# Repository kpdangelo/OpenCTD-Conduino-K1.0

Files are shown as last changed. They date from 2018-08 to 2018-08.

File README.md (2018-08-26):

# OpenCTD-Conduino-K1.0
OpenCTD with a Conduino inspired K1.0 graphite conductivity sensor

________________________________________
This CTD sensor started with the Open CTD plan. It evolved with the ideas from the UCSB researchers' Conduino repurposed-micro-USB probe. I was not able to solve the drift and consistency issues with the USB probe, so I have connected an Atlas Scientific K1.0 conductivity probe using the Conduino/AD5933 network analyzer based system. The benefit of using the AD5933 based system is that a calibration is required to convert the probe reading to Conductivity, providing a teaching opportunity on instrumentation. 
________________________________________

This project merges the Oceanography for Everyone Open CTD with the Conduino conductivity sensor, and an Atlas Scientific graphite probe.

Open CTD: https://github.com/OceanographyforEveryone/OpenCTD

Conduino: Marco Carminati, Paolo Luzzatto-Fegiz, Conduino: Affordable and high-resolution multichannel water conductivity sensor using micro USB connectors, In Sensors and Actuators B: Chemical, Volume 251, 2017, Pages 1034-1041, ISSN 0925-4005, https://doi.org/10.1016/j.snb.2017.05.184.

Follow the basic assembly instructions from OpenCTD along with the included instructions for constructing a Conduino.

PCBs can be ordered from OSHPARK, or Eagle and Gerber files are included here. Most of the assembly is with surface mount 0603 components. Doable without a stencil, solder paste and reflow, but easier with.

The system goes into a 2" PVC pipe and seals with Marine Epoxy and a 3D printed plug (file included here). See “Conduino K1.0 Pipe Assembly.pdf” file.

The Conduino PCB contains an analog mux that is not necessary when used with the K1.0 probe. To omit the mux, solder in 0 Ohm resistors R6 and R8 and leave U6 out. The mux was an attempt to zero out the drift seen when using the USB based probe. It didn’t work, but is left in for future experimentation.

The whole thing can be put together for around $300.

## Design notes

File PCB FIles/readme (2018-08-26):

These are the PCB files generated using Autodesk's Eagle CAD package.
*.sch and *.brd - Eagle Files
*.zip - gerbers
pdf's of the schematics too.

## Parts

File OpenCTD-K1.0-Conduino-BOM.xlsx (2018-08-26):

Part | Device | Package | Description
Conduino V03
C1,C4,C8,C16 | 1uF | 0603-CAP | Capacitor | $0.15 | $0.60 | https://www.digikey.com/product-detail/en/tdk-corporation/CGA3E1X7R1C105K080AC/445-12539-1-ND/3954205
C2,C10,C13,C17 | 100nF | 0603-CAP | Capacitor | $0.10 | $0.40 | https://www.digikey.com/product-detail/en/samsung-electro-mechanics/CL10B104KO8WPNC/1276-6582-1-ND/5961441
C9,C12 | 10uF | 0603-CAP | Capacitor | $0.36 | $0.72 | https://www.digikey.com/product-detail/en/samsung-electro-mechanics/CL10A106KP8NNNC/1276-1192-1-ND/3889278
C11 | 47nF | 0603-CAP | Capacitor | $0.22 | $0.22 | https://www.digikey.com/product-detail/en/kemet/C0603C473J4RACTU/399-9095-1-ND/3522612
J4 | BNC | BNC |  | $1.62 | $1.62 | https://www.digikey.com/product-detail/en/te-connectivity-amp-connectors/1-1337543-0/A97553-ND/1755940
R1,R2,R3,R5 | 49.9k | 0603-RES | Resistor | $0.35 | $1.40 | https://www.digikey.com/product-detail/en/panasonic-electronic-components/ERA-3AEB4992V/P49.9KDBCT-ND/3075986
R4,R10 | 20K | 0603-RES | Resistor | $0.19 | $0.38 | https://www.digikey.com/product-detail/en/yageo/RT0603DRD0720KL/311-20KDCT-ND/1035742
R6,R8 | 0 | 0603-RES | Resistor | $0.10 | $0.20 | https://www.digikey.com/product-detail/en/panasonic-electronic-components/ERJ-3GEY0R00V/P0.0GCT-ND/134711
R7 | 180 | 0603-RES | Resistor | $0.35 | $0.35 | https://www.digikey.com/product-detail/en/panasonic-electronic-components/ERA-3AEB181V/P180DBCT-ND/1466034
U1 | AD5933SSOP-16-AD | SSOP-16-AD |  | $35.96 | $35.96 | https://www.digikey.com/product-detail/en/analog-devices-inc/AD5933YRSZ/AD5933YRSZ-ND/756602
U2 | ADA8606-2 | SOIC_N |  | $3.71 | $3.71 | https://www.digikey.com/product-detail/en/analog-devices-inc/AD8606ARZ-REEL7/AD8606ARZ-REEL7CT-ND/3897177
U4 | LP5907 | SOT23-5L |  | $0.65 | $0.65 | https://www.digikey.com/product-detail/en/texas-instruments/LP5907QMFX-3.3Q1/296-40365-1-ND/5178242
U6 | TS3A24157 | VSSOP-10 |  | $1.05 | $1.05 | https://www.digikey.com/product-detail/en/texas-instruments/TS3A24157DGSR/296-22856-1-ND/1740004
PCB |  |  |  | $1.85 | $1.85 | https://www.oshpark.com/shared_projects/RJHBt9SN
OpenCTD-V04
R1 | 4.7K | AXIAL-0.4 | Resistor
U1 | QDUINO_MINI | QDUINO_MINI |  | $29.95 | $29.95 | https://www.sparkfun.com/products/13614
U2 | CONDUINO-V03 | CONDUINO_V03 |  |  |  | See above
U3 | SD-CARD-READER-MICRO-INOUT | SD-CARD-READER-105162 |  | $1.08 | $1.08 | https://www.digikey.com/product-detail/en/molex-llc/1051620001/WM14405CT-ND/6133135
 | Headers for Qduino |  |  | $0.81 | $0.81 | https://www.digikey.com/product-detail/en/sullins-connector-solutions/PPPC121LFBN-RC/S7045-ND/810184
PCB |  |  |  | $8.26 | $8.26 | https://www.oshpark.com/shared_projects/qzoyn3Dc
Pressure Sensor Single PCB
C1 | 0.1uF | 0603-CAP | Capacitor | $0.10 | $0.10 | https://www.digikey.com/product-detail/en/samsung-electro-mechanics/CL10B104KO8WPNC/1276-6582-1-ND/5961441
R1 | 10K | 0603-RES | Resistor | $0.18 | $0.18 | https://www.digikey.com/product-detail/en/panasonic-electronic-components/ERJ-PB3D1002V/P20397CT-ND/6214652
 | Pressure Sensor | MS580314BA01-00 |  | $13.82 | $13.82 | https://www.digikey.com/product-detail/en/sullins-connector-solutions/PPPC121LFBN-RC/S7045-ND/810184
PCB |  |  |  | $0.38 | $0.38 | https://www.oshpark.com/shared_projects/K8ReguM0
Conductivity Sensor
K-1.0 | Atlas Scientific |  |  | $139.00 | $139.00 | https://www.atlas-scientific.com/product_pages/probes/ec_k1-0.html
Temperature Sensor
 | Gikfun DS18B20 |  |  | $8.98 | $8.98 | https://www.amazon.com/gp/product/B00Q9YBIJI/ref=oh_aui_detailpage_o08_s00?ie=UTF8&psc=1
 | 2" Gripper |  |  | $9.39 | $9.39 | https://www.amazon.com/gp/product/B000VYNUAW/ref=oh_aui_detailpage_o08_s00?ie=UTF8&psc=1
 | 2 AH Li-Ion Battery |  |  | $12.50 | $12.50 | https://www.adafruit.com/product/2011
 |  |  |  | Total: | $273.56
Note: PCBs are ordered 3 at a time from OshPark, the single PCB price is shown here
Note: when ordering the batteries from Adafruit, you have to order something else to comply with LiIon shiping rules
 |  |  |  |  | $0.00

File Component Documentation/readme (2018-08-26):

Here are some useful datasheets, readily available, here for convenience

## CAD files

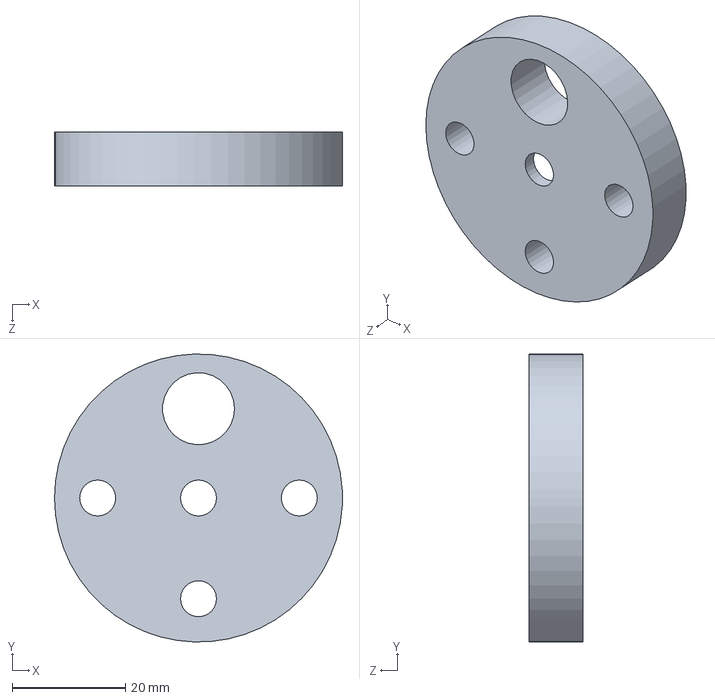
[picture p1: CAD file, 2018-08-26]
3D print/ctd base Pt.SLDPRT
50.8 x 50.8 x 9.53 mm

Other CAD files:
3D print/ctd base Pt.stl

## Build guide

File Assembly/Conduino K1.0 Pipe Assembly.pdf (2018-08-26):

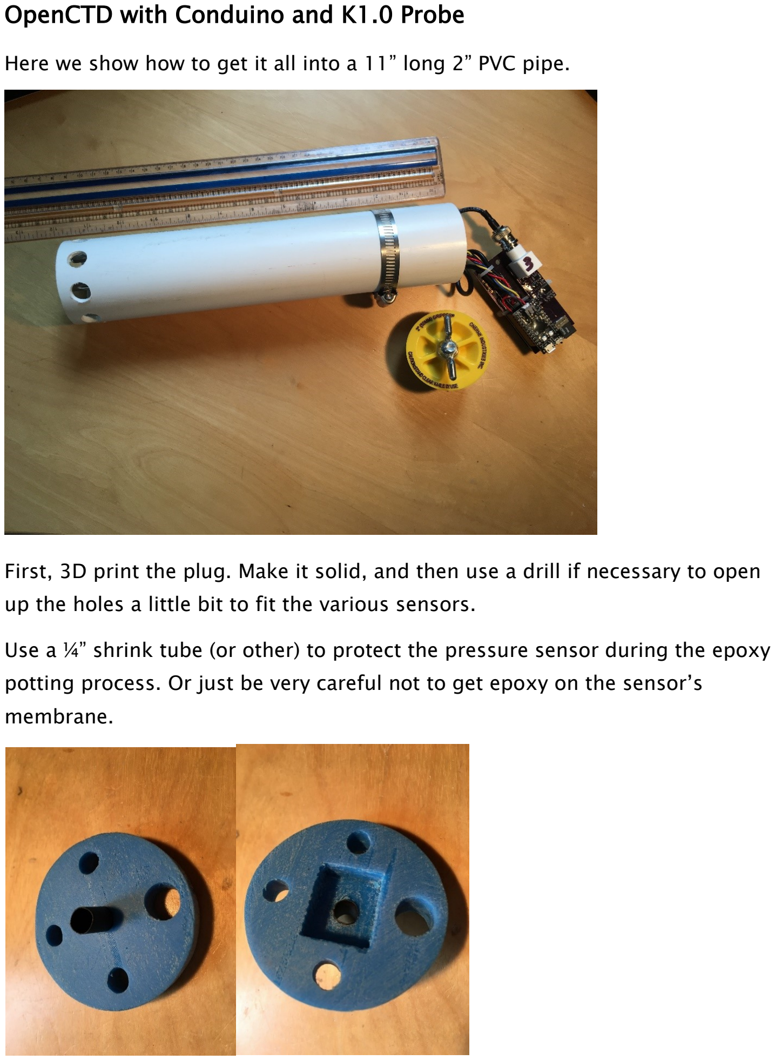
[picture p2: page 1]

OpenCTD with Conduino and K1.0 Probe

Here we show how to get it all into a 11” long 2” PVC pipe.

First, 3D print the plug. Make it solid, and then use a drill if necessary to open up the holes a little bit to fit the various sensors.

Use a ¼” shrink tube (or other) to protect the pressure sensor during the epoxy potting process. Or just be very careful not to get epoxy on the sensor’s membrane.

Secure the pressure sensor PCB in place (use clamps or something), and fill the void which is on the inside of the plug with Marine Epoxy.

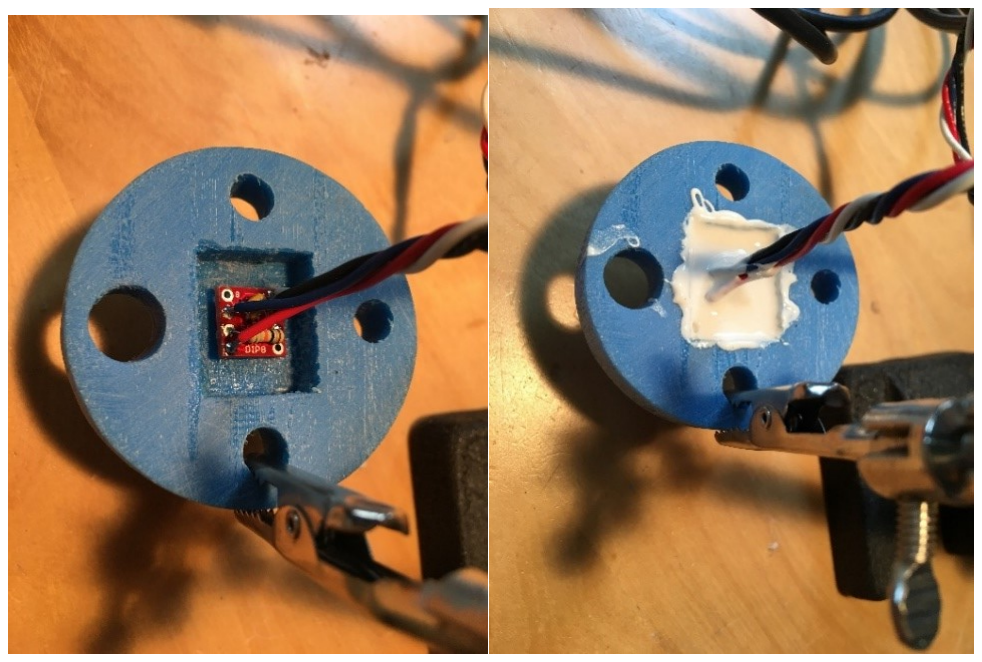
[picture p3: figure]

Next, fit the other sensors and use a little bit of Marine Epoxy to tack them in place, let that dry, and then coat the outside with a generous helping of Epoxy.

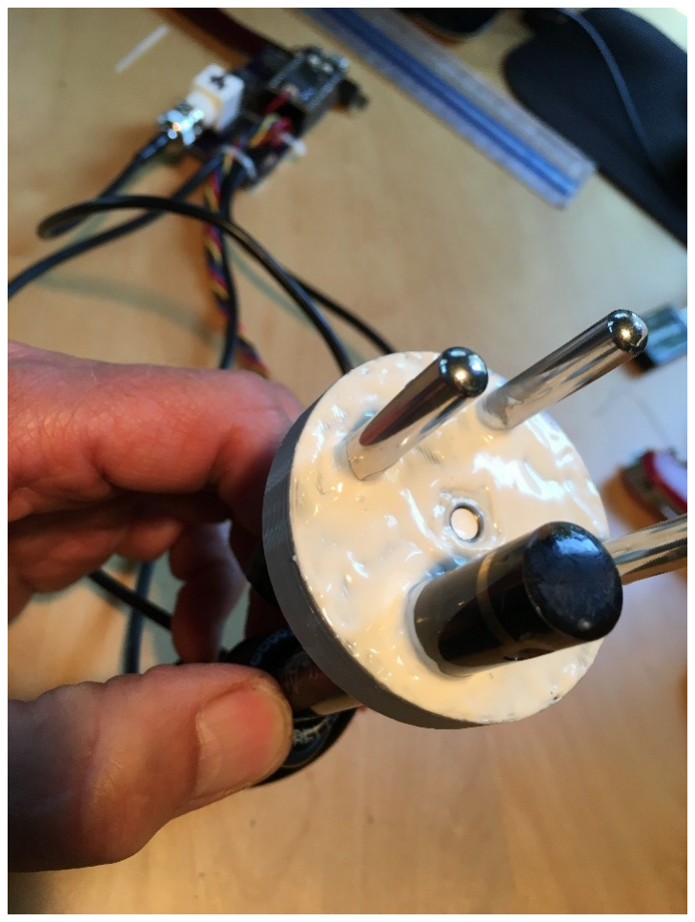
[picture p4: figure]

A nice way to handle the excess coax wire from the conductivity probe is to wrap it around the probe. Do this before you epoxy the base plate into the pipe.

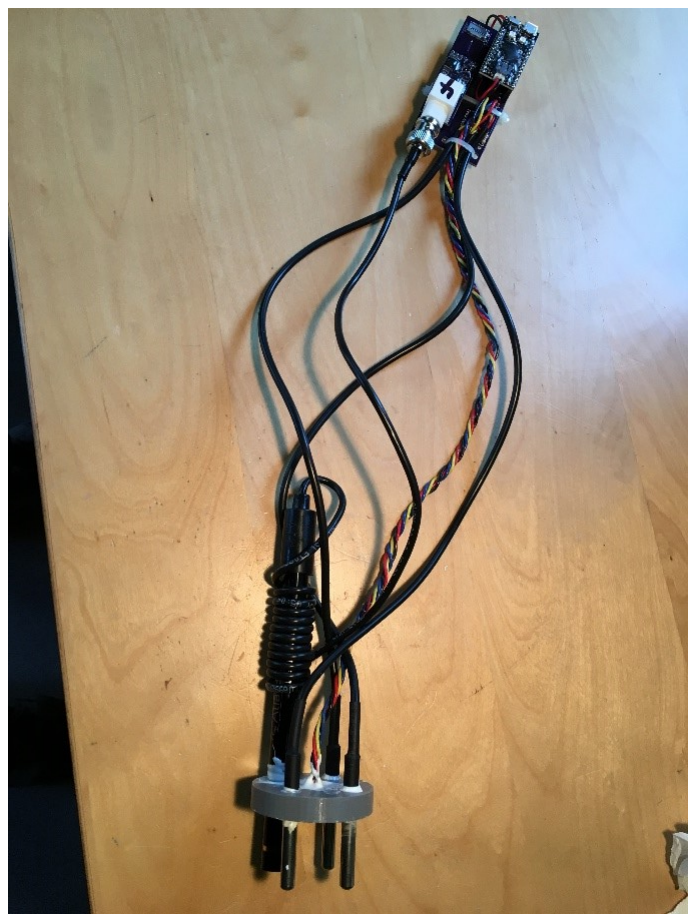
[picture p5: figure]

Epoxy the base plate into the pipe. Then go back and add epoxy so there is a nice seal around the exterior edge.

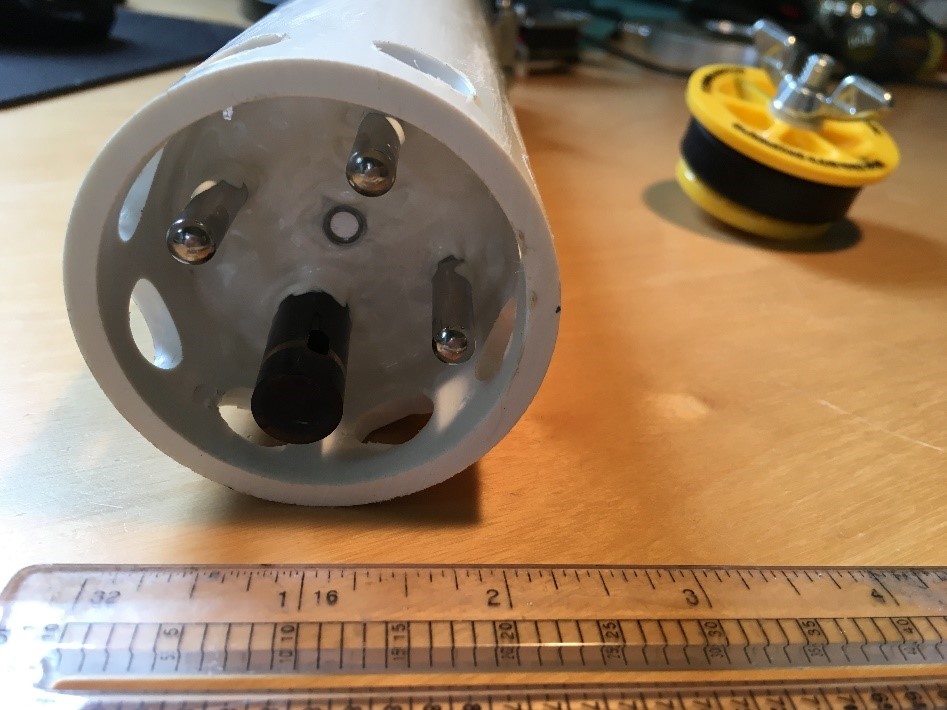
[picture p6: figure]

Cram the circuit board and the wires in the pipe. A twist of the circuit board is helpful to discover a fit. Attach the Gripper Plug and you’re ready to go. A hose clamp is a nice way to attach a cable to the probe.

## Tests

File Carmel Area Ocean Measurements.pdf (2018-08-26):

Carmel Area Ocean Measurements

The CTD sensor was used to sample various points along the Carmel City Beach and around Carmel Point and the Carmel River Lagoon. The region sampled is from 0 to 20 yards out at each location with the sensor hand held and moving about. Turbulence was moderate with breaking waves on the shore at Carmel Beach, but relatively smooth at the State Beach. Santa Lucia and the Dive Spot were heavy with kelp and the Dive spot had considerable surge.

Of note is that 4th street is near Pescadero Creek, which is not flowing to the ocean, but has pooled brackish water. 4th street is also at the beach along the Pebble Beach 10th fairway which is irrigated with reclaimed water. Potential reasons for the slightly lower salinity there.

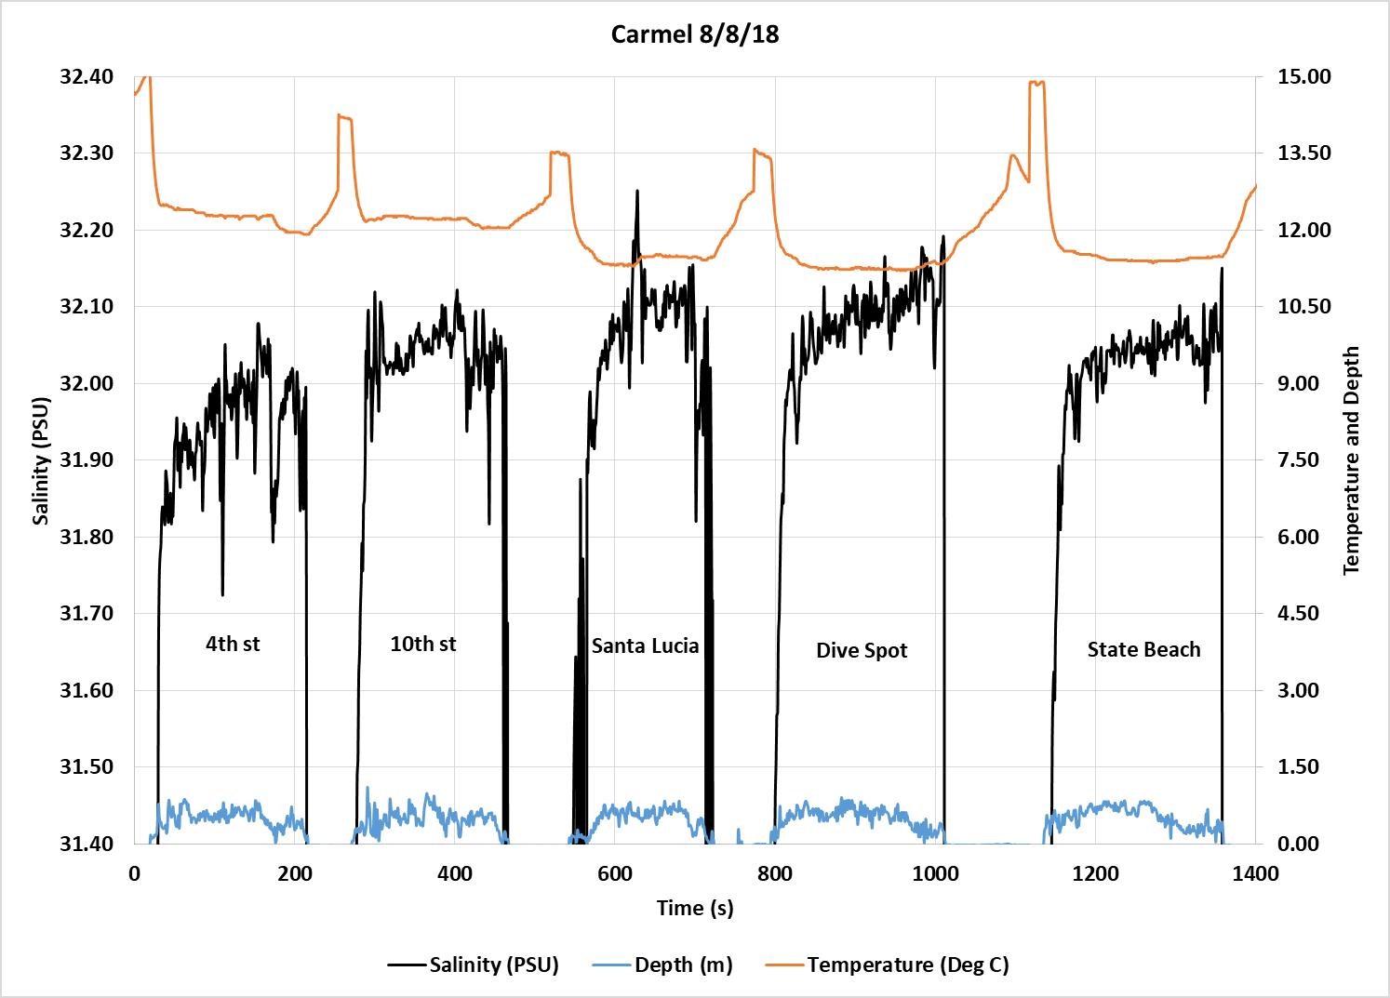
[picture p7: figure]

For fun, the Carmel River Lagoon was also sampled. Water there is not flowing into the ocean, and the surf is not flowing back into the lagoon. The lagoon has been stagnant for 2 months. A steady measurement is shown in the lagoon’s still environment vs. the beach’s breaking waves.

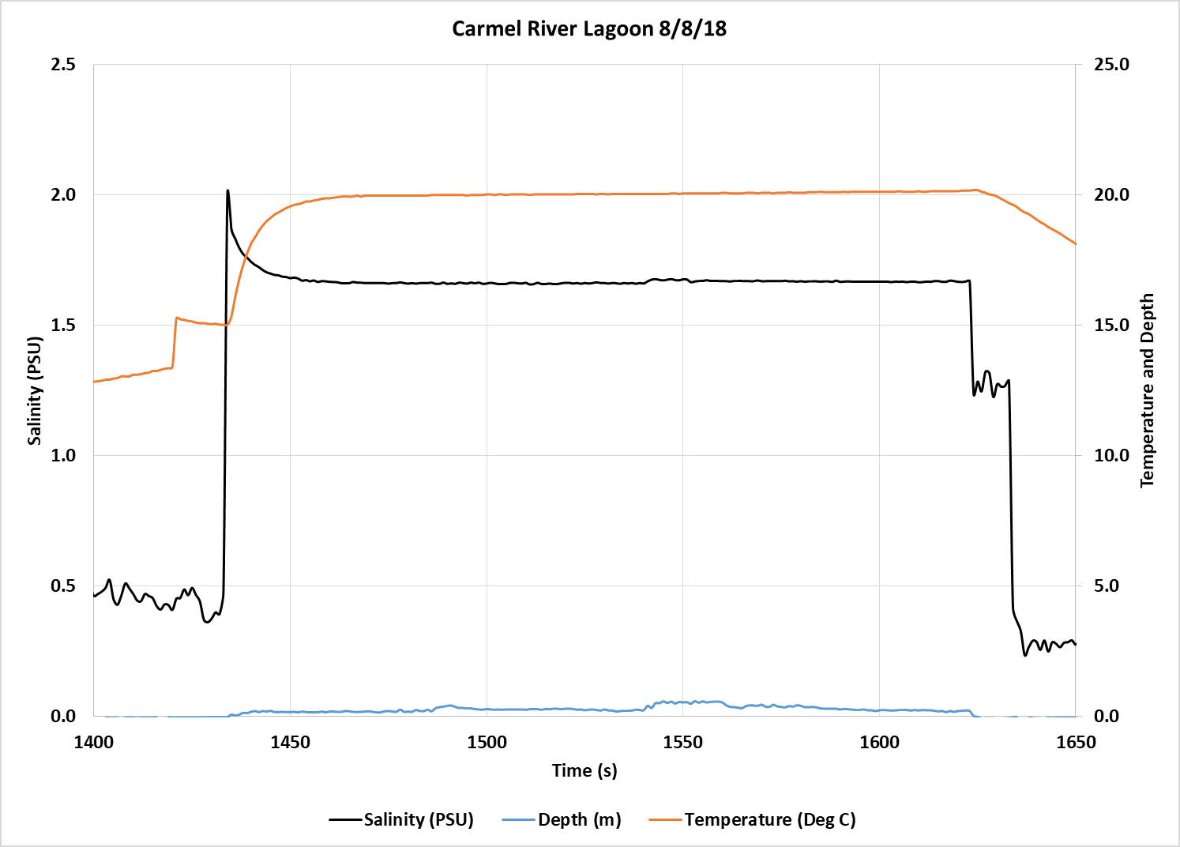
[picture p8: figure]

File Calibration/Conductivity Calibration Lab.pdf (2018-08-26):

Conductivity Calibration Lab

All conductivity sensors require calibration. This is because they use a sensor that measures impedance (a measure of the resistivity of a solution caused by the ions in solution) rather than conductivity directly. In our case we are interested in the conductivity of sea water which we will use to derive a salinity value. Calibration is necessary to develop a curve to translate a raw resistivity measurement into conductivity.

We start with known concentrations of salt in parts per thousand (ppt). The resistivity of the known solution is measured with our probe, and along with temperature and pressure measurements, we can derive the conductivity. We will use 5 different known concentrations to create a curve of conductivity vs. raw resistivity (actually a scaled resistivity to put the numbers in a nicer range). The curve will resemble a straight line, but with a little bit of a bow, so we will use Excel to fit a polynomial curve to it to be more exact in our conductivity vs. raw resistivity transfer function. Then we’ll use that equation to give us conductivity out in the field.

Excel is used to help us keep track of our calibration.

To start, let’s use a table to keep track of the salt concentrations:

First weigh out 110g of Kosher Salt (because it is pure and readily available). Next add water to achieve a given concentration.

For instance, to achieve 40 ppt (0.040 concentration) we need to satisfy the relation in weights (we’ll use grams),

salt
salt + water

= 0.040

A table is super handy so we can use the actual weights used since it’s difficult, and unnecessary to hit the numbers exactly using the scale. Enter the actual weight and let Excel do the concentration calculation.

For this calibration, 110g of salt was used, which resulted in this table:

Concentration | Total Weight | Actual Weight Increment | Target Weight Increment
0.03658 | 3007 | 3007 | 3000
0.03201 | 3436 | 429 | 430
0.02729 | 4031 | 595 | 570
0.02279 | 4826 | 795 | 800
0.01826 | 6025 | 1199 | 1200

Once you’ve added the water and achieved a first known concentration, use a pump inside the vessel, cover it (with foil for example) and let it circulate a good hour or so to let the salt dissolve and the air bubbles to disappear. Use a low power pump so as not to heat the water, or add air.

Turn on the probe, and make sure you get the green light which indicates the micro-SD card is properly seated. Soak the probe at each concentration, adding incremental water for each soak. For the following calibration data, the probe was soaked for 10 minutes at each concentration.

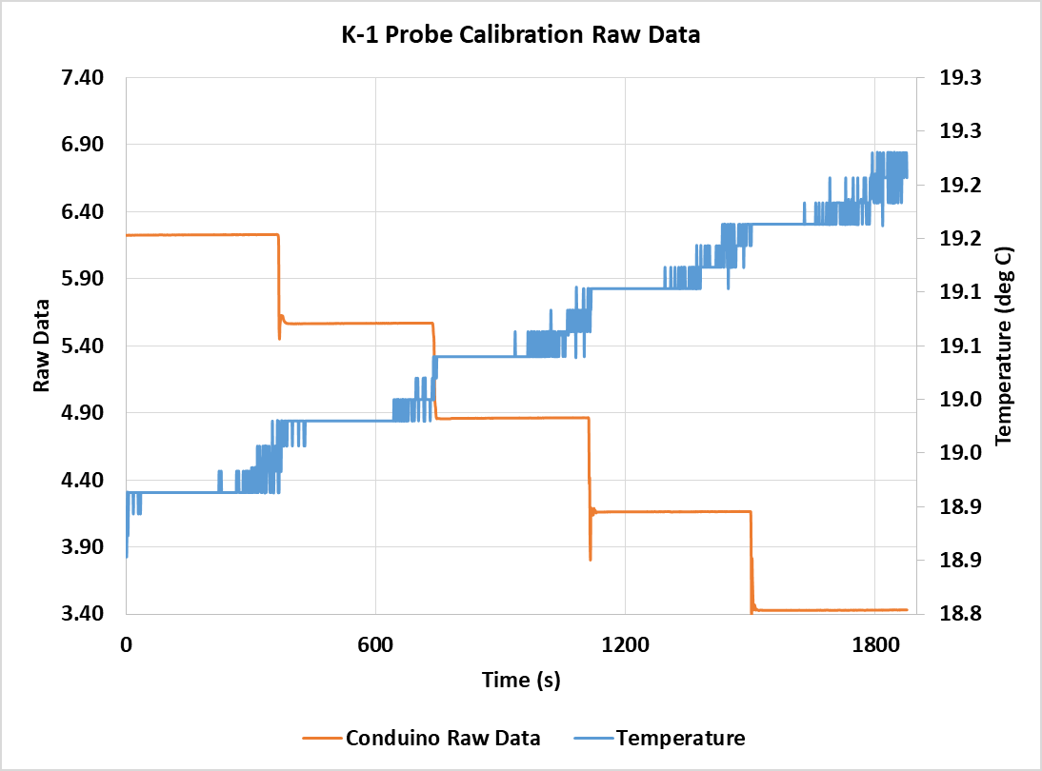
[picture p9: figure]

Here, you can see the orange curve stepping down in resistivity after each increment of water is added. The temperature happens to have a slight upward trajectory which is no big deal.

Next, create a table by translating the known salinity and temperature to conductivity using a calculator at salinometry.com: http://salinometry.com/stp-conductivity-calculator/

For the calculator, enter the known salinity in PPT, enter temperature in degrees C, and pressure in dBar (deci-bar). Our pressure sensor reports in mbar (millibar), so divide that number by 100 (since 1000mBar=10dBar).

Known Salinity (PPT) | temp | Conduino Raw Data | Conductivity (salinometry.com)
18.26 | 19.20 | 3.43 | 26.187
22.79 | 19.13 | 4.16 | 31.981
27.29 | 19.06 | 4.86 | 37.580
32.01 | 18.99 | 5.57 | 43.303
36.58 | 18.93 | 6.229 | 48.717

From this table the transfer function is plotted

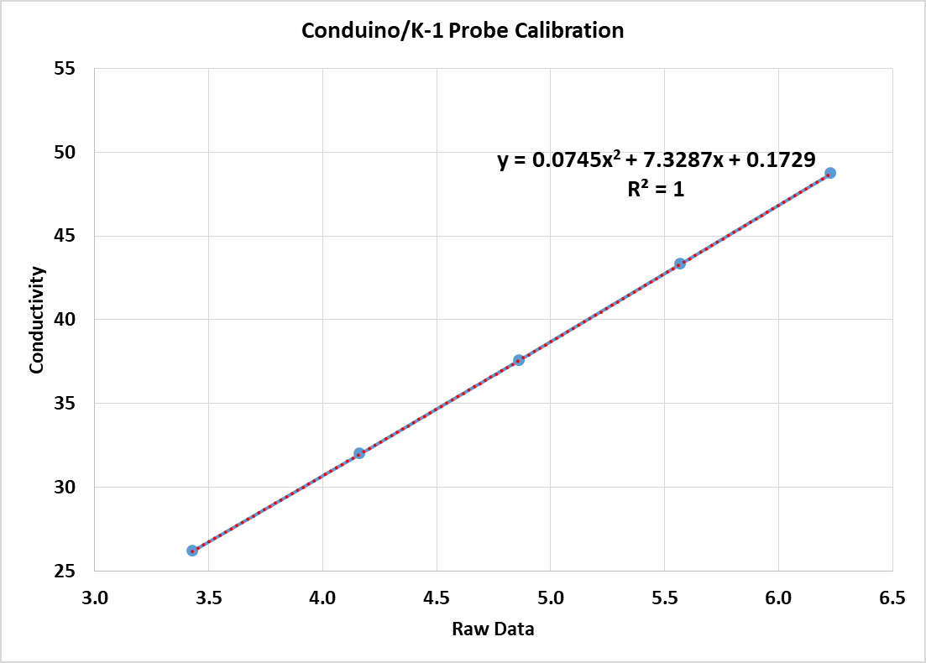
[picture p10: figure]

Here, the “Trendline” feature in Excel is used. You can choose from many options including linear, exponential, power, polynomial, etc. Choose polynomial and you get a great fit. Excel displays R², the coefficient of determination, typically used in statistical analysis where you’re trying to get a curve to represent a cluster of data. When R²=1, it’s as good as it gets.

The equation,

y = 0.0745x

2 + 7.3287x + 0.1729

can now be embedded into the Arduino program resident in the probe electronics to report the conductivity value directly.

After taking the now calibrated probe for a spin in the Carmel surf, and then calculating salinity using the Excel conversion template, we get the following response:

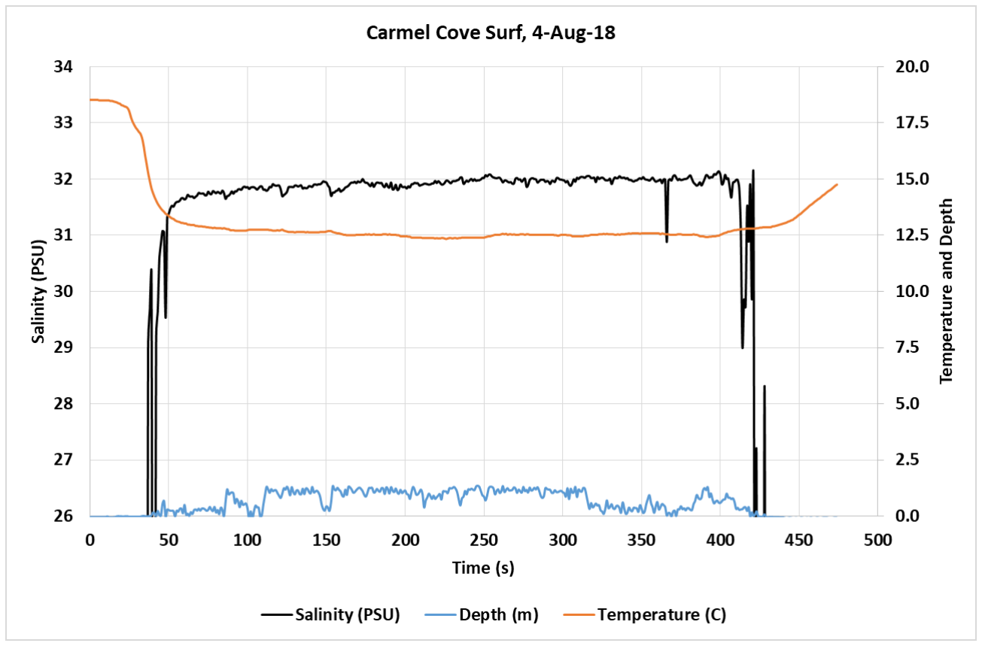
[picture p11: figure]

No surprises here, it’s salty and cold!

8/26/18

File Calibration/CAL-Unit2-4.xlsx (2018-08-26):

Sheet: 2
time | Tave | Conduino | Salt (g) | 110 |  |  | Salinity (PPT) | t1 | Conduino | Conductivity (salinometry.com) | *1,000 | back check: | PSU from Conversion Template | diff | raw data here
0 | 18.9 | 6.26 |  |  |  |  | 18.26 | 19.25 | 3.44 | 26.215 | 26215.2 |  | 19.85 | 8.73% | 0 | 1019.1 | 18.81 | 18.94 | 19 | 48214.42 | 6.2595
1 | 18.9 | 6.26 | Concentration | Total Weight | Actual Weight Increment | Target Weight Increment | 22.79 | 19.18 | 4.18 | 32.016 | 32016.1 |  | 24.83 | 8.96% | 1 | 1019.3 | 18.81 | 18.94 | 19 | 48210.75 | 6.259
2 | 18.9 | 6.26 | 0.03658 | 3007 | 3007 | 3000 | 27.29 | 19.12 | 4.89 | 37.629 | 37628.6 |  | 29.78 | 9.12% | 2 | 1019.1 | 18.81 | 18.94 | 19.06 | 48215.7 | 6.2596
3 | 18.9 | 6.26 | 0.03201 | 3436 | 429 | 430 | 32.01 | 19.05 | 5.60 | 43.359 | 43359.3 |  | 34.83 | 8.80% | 3 | 1019.4 | 18.81 | 18.94 | 19.06 | 48210.75 | 6.259
4 | 18.9 | 6.26 | 0.02729 | 4031 | 595 | 570 | 36.58 | 18.99 | 6.267 | 48.780 | 48780.3 |  | 39.82 | 8.86% | 4 | 1019.3 | 18.81 | 18.94 | 19.06 | 48219.36 | 6.2601
5 | 18.9 | 6.26 | 0.02279 | 4826 | 795 | 800 |  |  |  |  |  |  |  |  | 5 | 1019.1 | 18.81 | 18.94 | 19.06 | 48216.99 | 6.2598
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

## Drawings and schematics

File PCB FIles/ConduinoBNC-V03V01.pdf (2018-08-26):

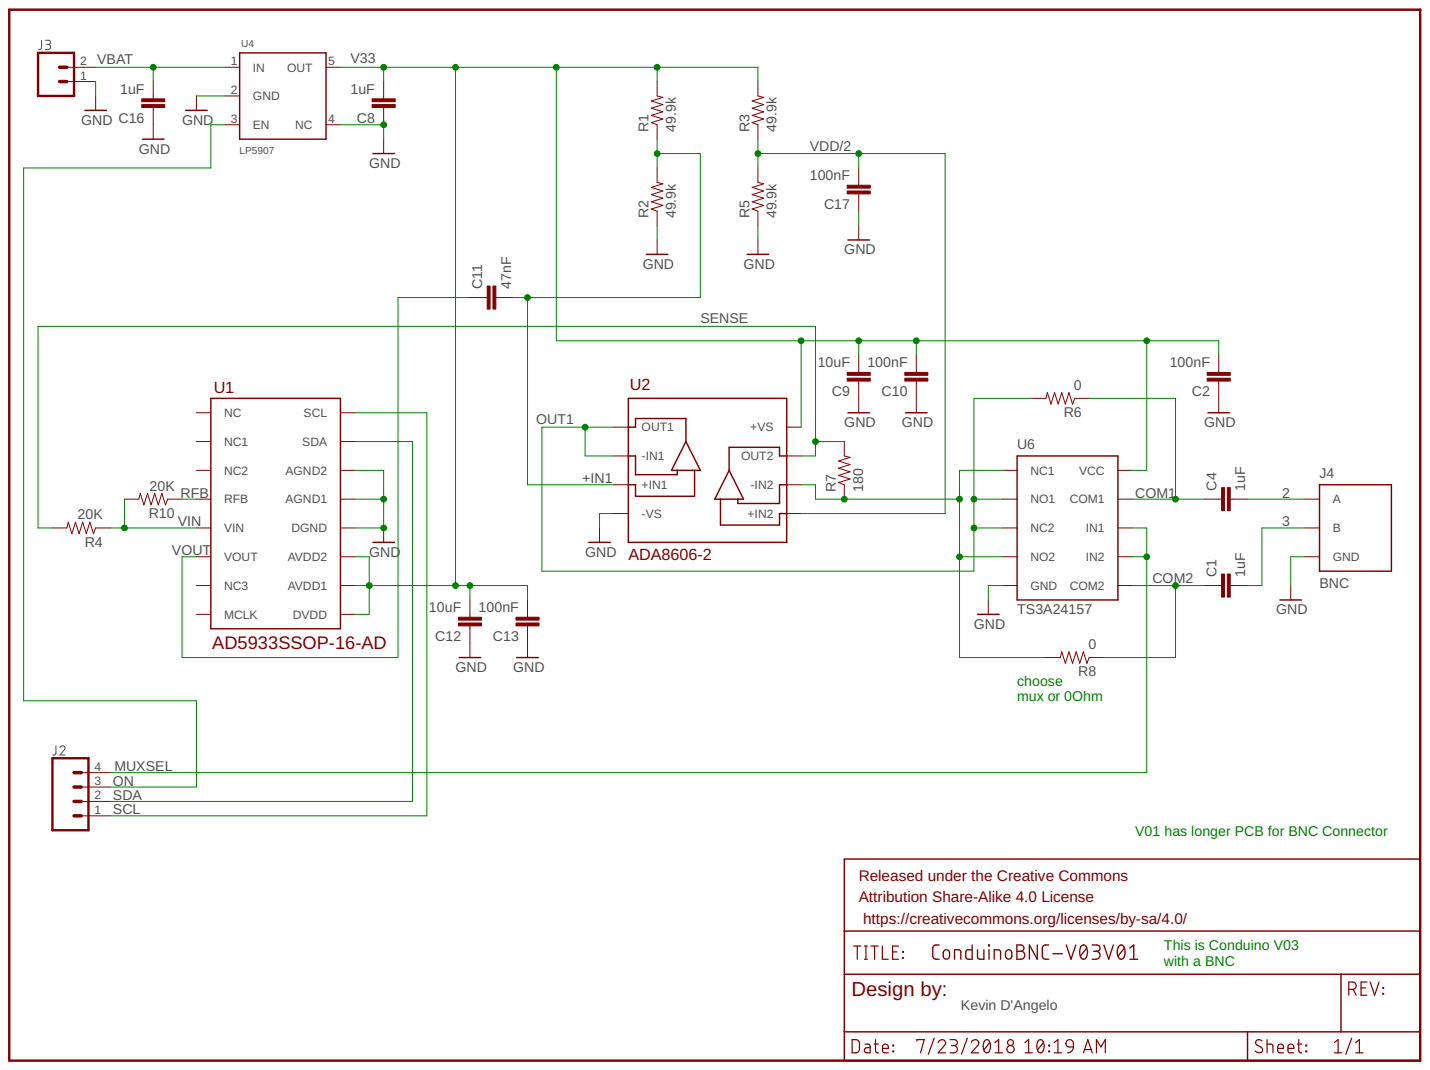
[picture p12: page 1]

V01 has longer PCB for BNC Connector

Released under the Creative Commons Attribution Share-Alike 4.0 License

https://creativecommons.org/licenses/by-sa/4.0/

This is Conduino V03 with a BNC

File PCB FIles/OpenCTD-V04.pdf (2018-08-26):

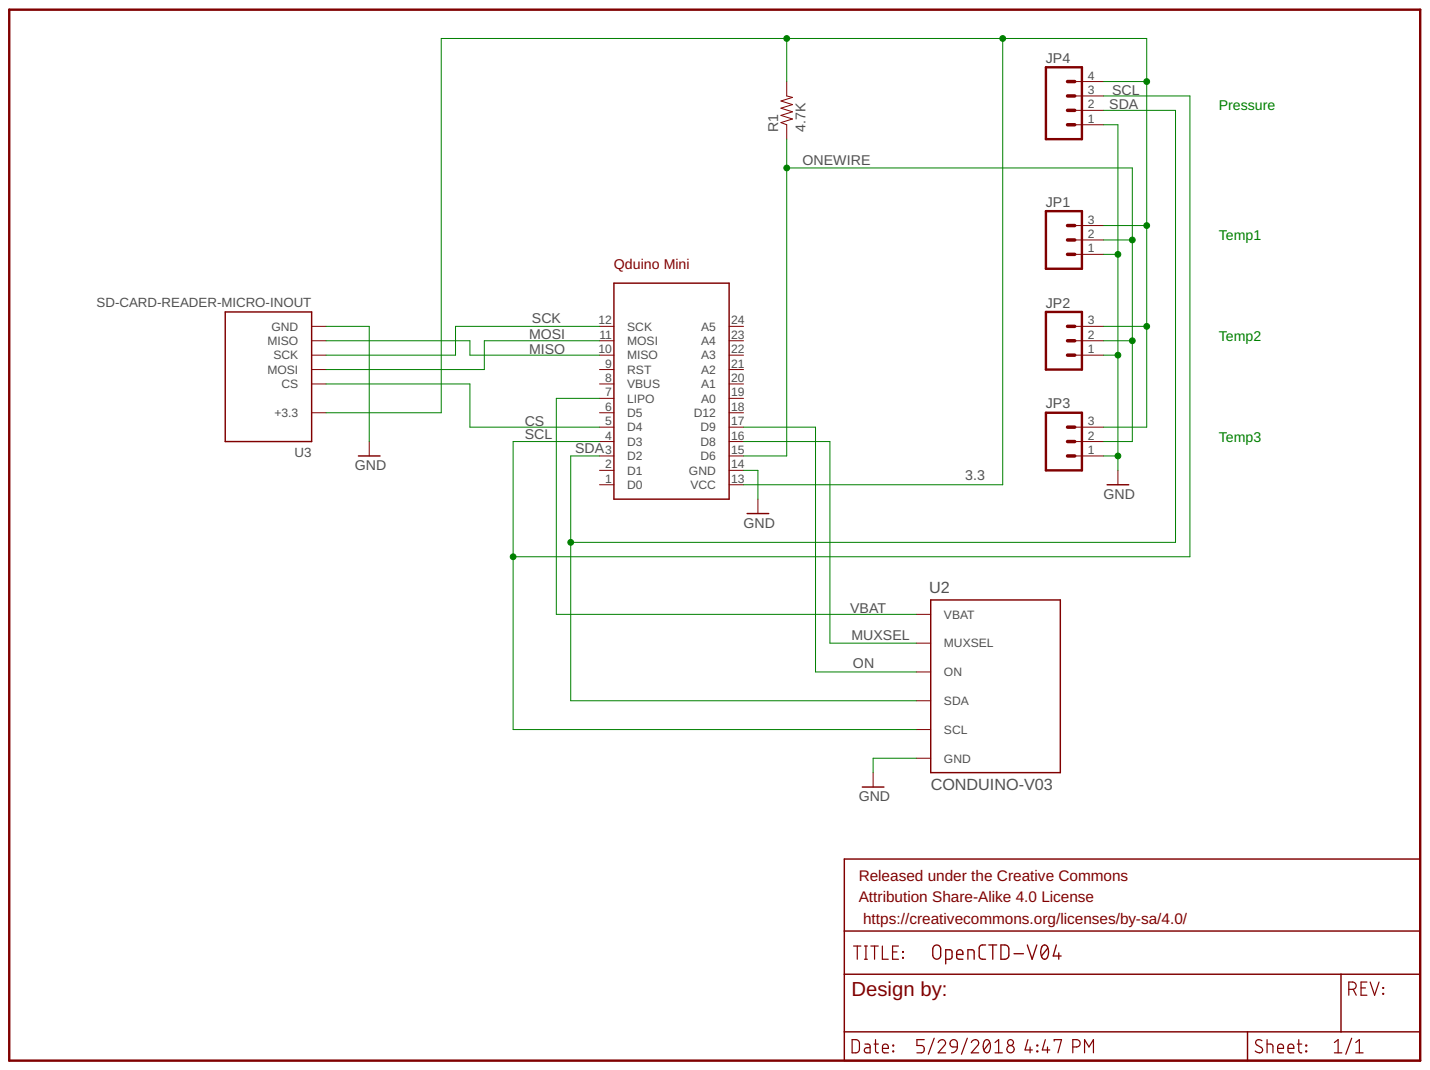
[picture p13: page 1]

2 SDA

SD-CARD-READER-MICRO-INOUT

SCL SDA ONMUXSEL VBAT

Released under the Creative Commons Attribution Share-Alike 4.0 License

https://creativecommons.org/licenses/by-sa/4.0/

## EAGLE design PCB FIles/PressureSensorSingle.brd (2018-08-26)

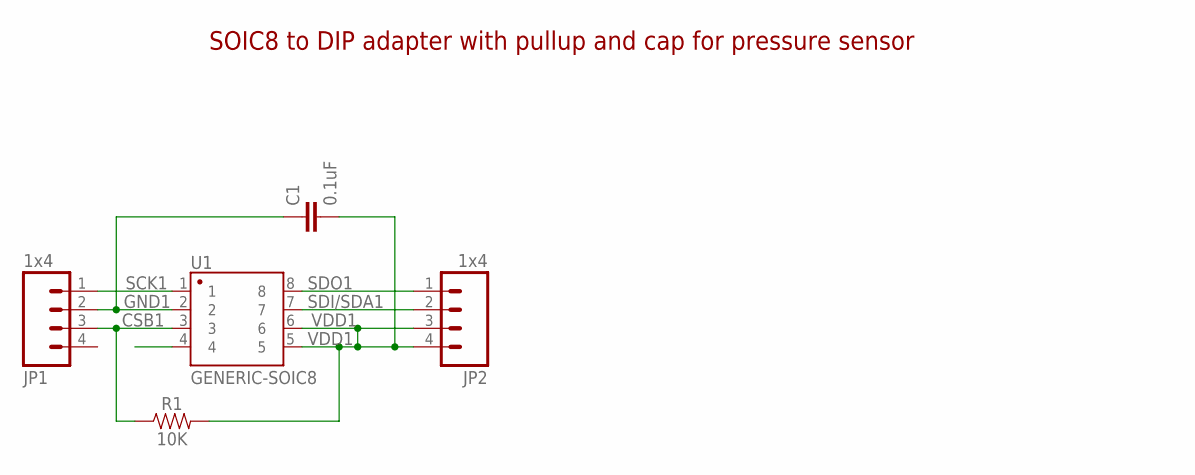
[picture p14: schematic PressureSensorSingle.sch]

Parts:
C1: 0.1uF; 0603
JP1: 1x4; 1X04_NO_SILK
JP2: 1x4; 1X04_NO_SILK_ALL_ROUND
R1: 10K; 0603
U1: GENERIC-SOIC8; SO08-UNIVERSAL

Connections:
CSB1: JP1.3, R1.1, U1.3
GND1: C1.1, JP1.2, U1.2
NC1: U1.4
SCK1: JP1.1, U1.1
SDI/SDA1: JP2.2, U1.7
SDO1: JP2.1, U1.8
VDD1: C1.2, JP2.3, JP2.4, R1.2, U1.5, U1.6

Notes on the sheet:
SOIC8 to DIP adapter with pullup and cap for pressure sensor

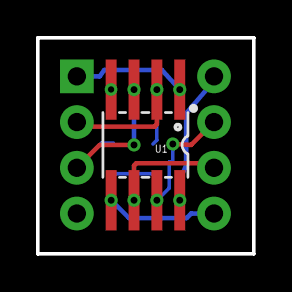
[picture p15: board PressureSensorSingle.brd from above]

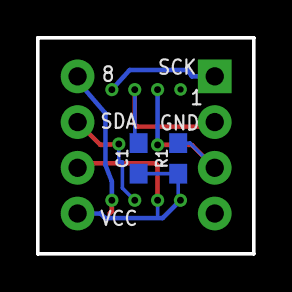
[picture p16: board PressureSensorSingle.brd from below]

Board: 2 copper layers, 12.0 x 12.0 mm, 5 parts (2 on the bottom side), 6 nets.

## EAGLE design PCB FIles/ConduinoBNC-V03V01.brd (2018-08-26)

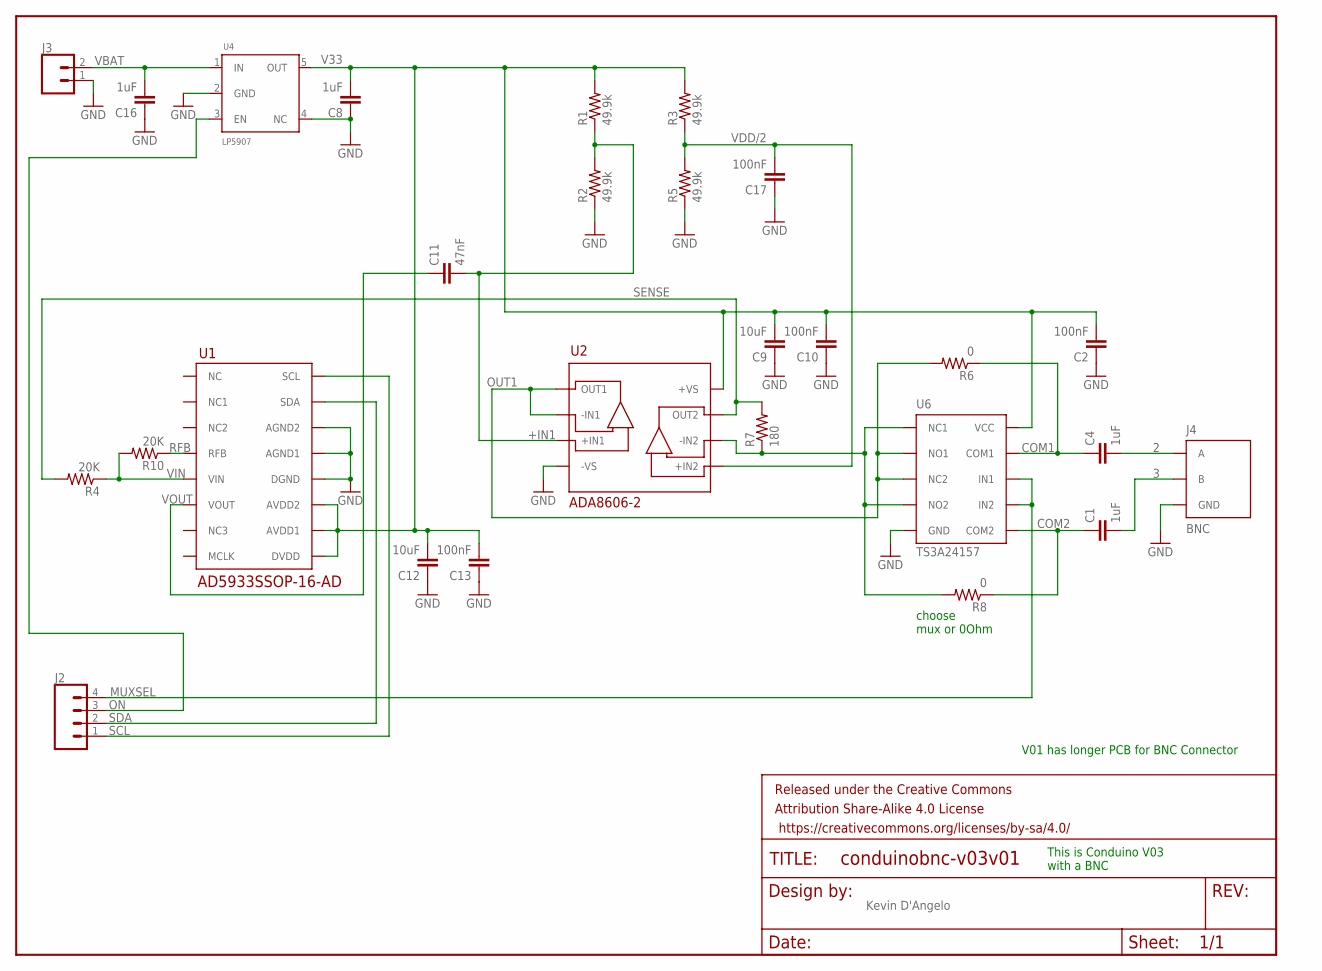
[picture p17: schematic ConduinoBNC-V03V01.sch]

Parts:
C1, C4, C8, C16: 1uF; 0603-CAP
C2, C10, C13, C17: 100nF; 0603-CAP
C9, C12: 10uF; 0603-CAP
C11: 47nF; 0603-CAP
FRAME1: FRAME-LETTER; CREATIVE_COMMONS
J2: CONN_041X04_NO_SILK; 1X04_NO_SILK
J3: CONN_021X02_NO_SILK; 1X02_NO_SILK
J4: BNC
R1, R2, R3, R5: 49.9k; 0603-RES
R4, R10: 20K; 0603-RES
R6, R8: 0; 0603-RES
R7: 180; 0603-RES
U1: AD5933SSOP-16-AD; SSOP-16-AD
U2: ADA8606-2; SOIC_N
U4: LP5907; SOT23-5L
U6: TS3A24157; VSSOP-10

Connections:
2: C4.2, J4.P$1 (A)
3: C1.2, J4.P$2 (B)
+IN1: C11.2, R1.1, R2.2, U2.P$3 (+IN1)
-IN2: R7.1, R8.2, U2.P$6 (-IN2), U6.P$1 (NC1), U6.P$4 (NO2)
COM1: C4.1, R6.1, U6.P$9 (COM1)
COM2: C1.1, R8.1, U6.P$6 (COM2)
GND: C2.1, C8.1, C9.1, C10.1, C12.1, C13.1, C16.1, C17.1, J3.1, J4.P$3 (GND), J4.P$4 (GND), R2.1, R5.1, U1.P$12 (DGND), U1.P$13 (AGND1), U1.P$14 (AGND2), U2.P$4 (-VS), U4.2 (GND), U4.4 (NC), U6.P$5 (GND)
MUXSEL: J2.4, U6.P$7 (IN2), U6.P$8 (IN1)
ON: J2.3, U4.3 (EN)
OUT1: R6.2, U2.P$1 (OUT1), U2.P$2 (-IN1), U6.P$2 (NO1), U6.P$3 (NC2)
RFB: R10.1, U1.P$4 (RFB)
SCL: J2.1, U1.P$16 (SCL)
SDA: J2.2, U1.P$15 (SDA)
SENSE: R4.2, R7.2, U2.P$7 (OUT2)
V33: C2.2, C8.2, C9.2, C10.2, C12.2, C13.2, R1.2, R3.2, U1.P$9 (DVDD), U1.P$10 (AVDD1), U1.P$11 (AVDD2), U2.P$8 (+VS), U4.5 (OUT), U6.P$10 (VCC)
VBAT: C16.2, J3.2, U4.1 (IN)
VDD/2: C17.2, R3.1, R5.2, U2.P$5 (+IN2)
VIN: R4.1, R10.2, U1.P$5 (VIN)
VOUT: C11.1, U1.P$6 (VOUT)

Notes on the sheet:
choose mux or 0Ohm
This is Conduino V03 with a BNC
Kevin D'Angelo
V01 has longer PCB for BNC Connector

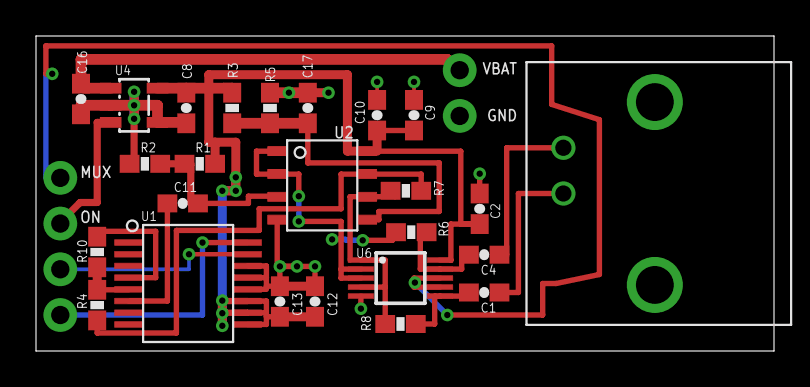
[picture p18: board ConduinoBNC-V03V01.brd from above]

Board: 2 copper layers, 41.0 x 17.5 mm, 28 parts (0 on the bottom side), 19 nets.

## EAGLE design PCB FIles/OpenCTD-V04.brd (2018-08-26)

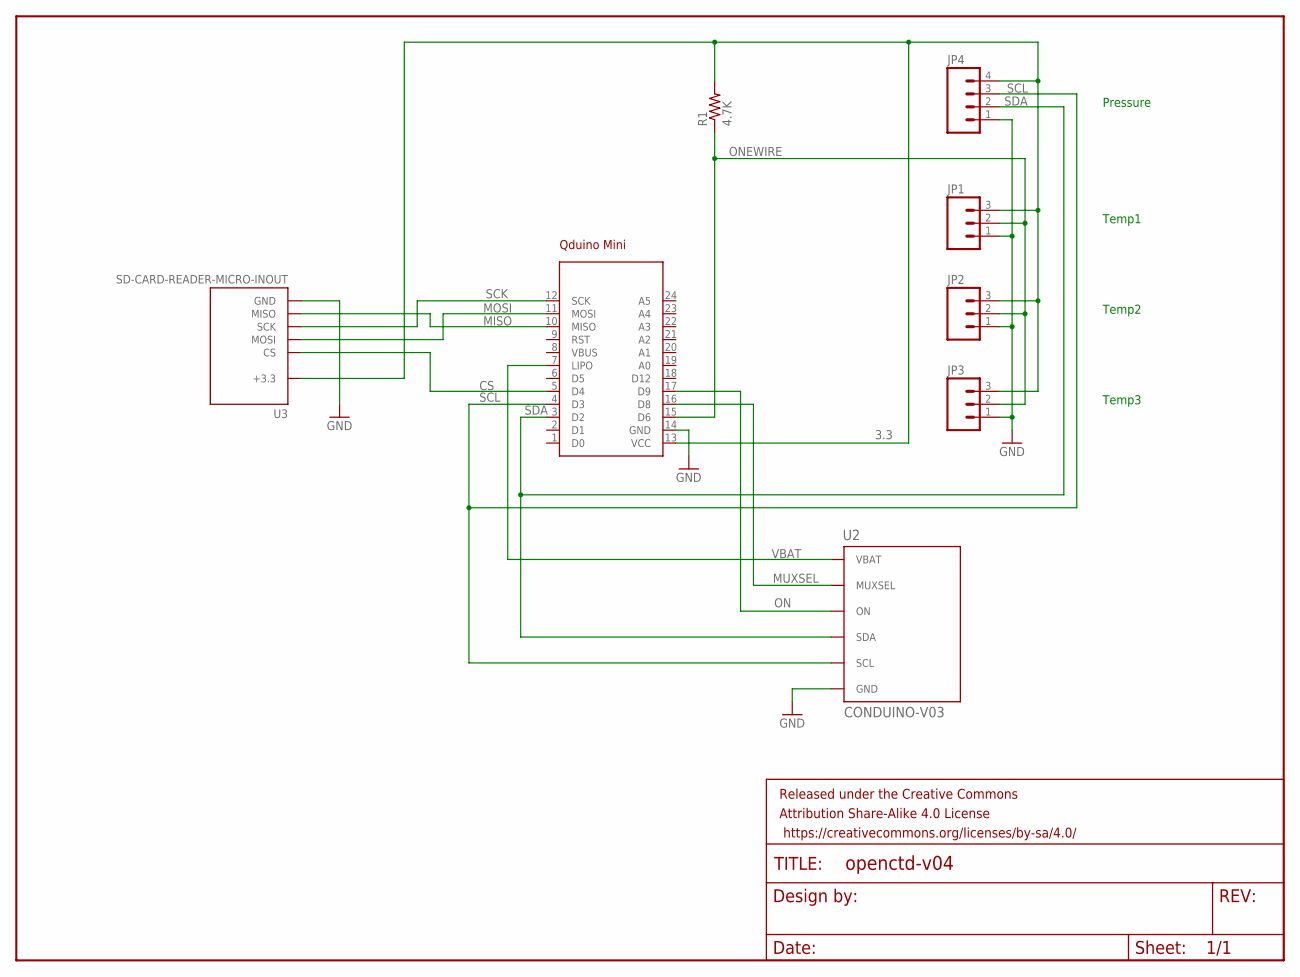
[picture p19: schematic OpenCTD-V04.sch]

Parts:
FRAME1: FRAME-LETTER; CREATIVE_COMMONS
JP1, JP2, JP3: M031X03_NO_SILK; 1X03_NO_SILK
JP4: M041X04_NO_SILK; 1X04_NO_SILK
R1: 4.7K; AXIAL-0.4
U1: QDUINO_MINI
U2: CONDUINO-V03; CONDUINO_V03
U3: SD-CARD-READER-MICRO-INOUT; SD-CARD-READER-105162

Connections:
3.3: JP1.3, JP2.3, JP3.3, JP4.4, R1.P$2 (2), U1.13 (VCC), U3.P$4 (+3.3)
CS: U1.5 (D4), U3.P$2 (CS)
GND: JP1.1, JP2.1, JP3.1, JP4.1, U1.14 (GND), U2.5 (GND), U3.G1 (GND), U3.G2 (GND), U3.G3 (GND), U3.G4 (GND), U3.P$6 (GND)
MISO: U1.10 (MISO), U3.P$7 (MISO)
MOSI: U1.11 (MOSI), U3.P$3 (MOSI)
MUXSEL: U1.16 (D8), U2.4 (MUXSEL)
ON: U1.17 (D9), U2.3 (ON)
ONEWIRE: JP1.2, JP2.2, JP3.2, R1.P$1 (1), U1.15 (D6)
SCK: U1.12 (SCK), U3.P$5 (SCK)
SCL: JP4.3, U1.4 (D3), U2.1 (SCL)
SDA: JP4.2, U1.3 (D2), U2.2 (SDA)
VBAT: U1.7 (LIPO), U2.6 (VBAT)

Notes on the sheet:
Pressure
Temp1
Temp2
Temp3

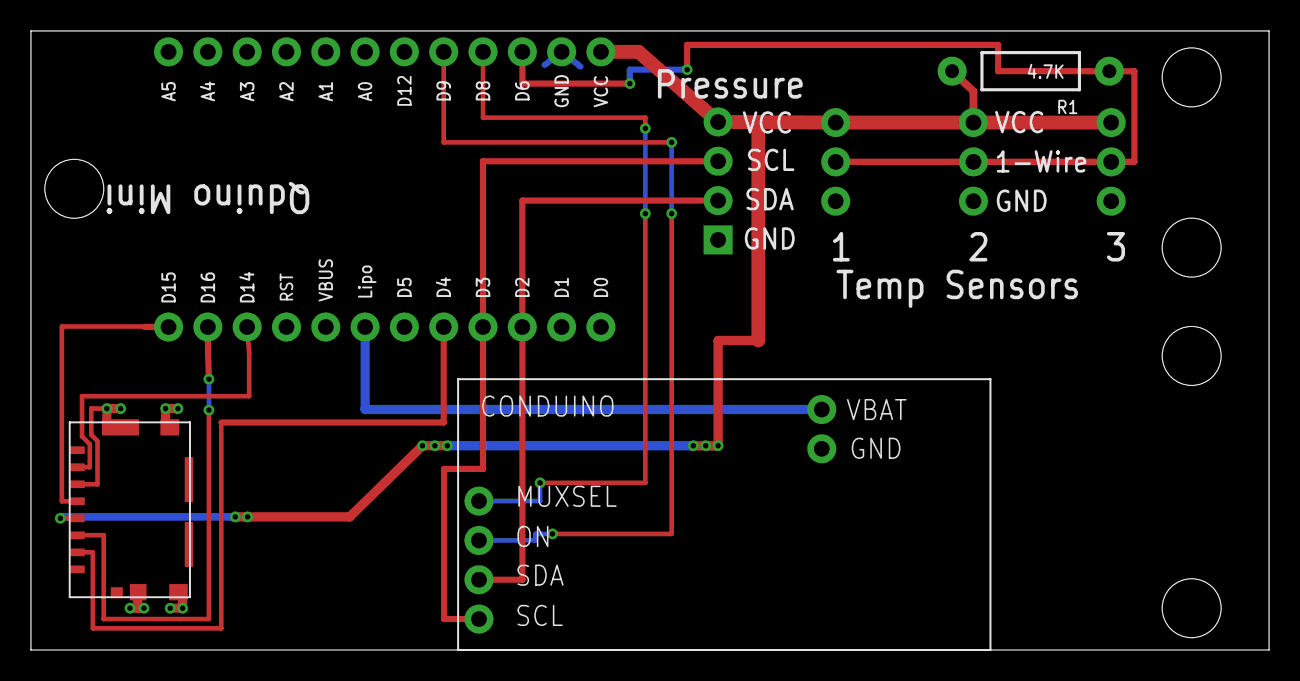
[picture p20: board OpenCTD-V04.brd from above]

Board: 2 copper layers, 80.0 x 40.0 mm, 9 parts (0 on the bottom side), 12 nets.

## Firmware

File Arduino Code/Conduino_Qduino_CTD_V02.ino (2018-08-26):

///////////////////////////////////////////////////////////////////////////////////////////////////////////////
/*
   Conduino_Qduino_CTD_V02

   This sketch is adapted from the open CTD from Oceanography for Everyone
   http://www.oceanographyforeveryone.com/
   https://github.com/OceanographyforEveryone/OpenCTD

   Sensors are
   MS5803 pressure sensor
   Dallas 1-wire temperature sensors
   Conduino conductivity sensor which uses the AD5933 Network Analyzer

   Marco Carminati, Paolo Luzzatto-Fegiz,
   Conduino: Affordable and high-resolution multichannel water conductivity sensor using micro USB connectors,
   In Sensors and Actuators B: Chemical, Volume 251, 2017, Pages 1034-1041, ISSN 0925-4005,
   https://doi.org/10.1016/j.snb.2017.05.184.

   output format on SD card:
   TimeStamp(seconds) Pressure(mbar) Temperature 1 2 3 (deg C) Conductivity (us/cm)

   Kevin D'Angelo
   7/22/18
*/
/////////////////////////////////////////////////////////////////////////////////////////////////////////////////
#include <Wire.h>
#include "Qduino.h"
qduino q;
#include <MS5803_14.h>
#include <avr/wdt.h>      // watch dog timer
///////////////////////////////////////////////////////////////////////////////////////////////
//  Sample Interval
//  loop takes about 810ms, so the sample interval needs to be greater than that.
//  The bulk of the time, 622ms, is used to communicate with the 1-wire temperature sensors.
//  watch dog timer is continuously reset while waiting for sample interval.
////////////////////////////////////////////////////////////////////////////////////////////////
#define SampleInterval 1000      // 1000 ms
///////////////////////////////////////////////////////////////////////////////////////////////////////////////
// Temperature and pressure releated
///////////////////////////////////////////////////////////////////////////////////////////////////////////////
//OneWire is used to get data from both temperature and conductivity sensors
#include <OneWire.h>  //CAN WE MAKE THIS LIBRARY SMALLER?

//DallasTemperature is used to query the temeprature sensors
#include <DallasTemperature.h>   //CAN WE MAKE THIS LIBRARY SMALLER?

// For the SD card reader.
#include <SPI.h>
#include <SD.h>

// Declare global variables.
float tempA;
float tempB;
float tempC;

OneWire oneWire(6);        // Define the OneWire port for temperature.
DallasTemperature sensors(&oneWire);  // Define DallasTemperature input based on OneWire.

MS_5803 sensor = MS_5803(4096);     // pressure sensor
double pressure_abs; // define absolute pressure variable.

/////////////////////////////////////////////////////////////////////////////////
//    CONDUINO RELATED
///////////////////////////////////////////////////////////////////////////////
// The user must calibrate the AD5933 system for a known impedance range to determine the gain factor

// polynomial coefficients for conversion from conduino reading to conductivity
// conductivity = CA*X^2 + CB*X + CC, where X is the conduino reading
// Unit 1
//#define CA 0.0851
//#define CB 7.1241
//#define CC 0.2871
// Unit 2
//#define CA 0.0702
//#define CB 7.3119
//#define CC 0.2013
// Unit 3 
//#define CA 0.0851
//#define CB 7.1241
//#define CC 0.2871
// Unit 4
#define CA 0.0745
#define CB 7.3287
#define CC 0.1729

#define AD5933_ADDR 0x0D

double ConduinoReading;
double Conductivity;
double magnitude;
double phase;
double impedance;
double gain = 5.825 * pow(10, -6); //calibrated with 180.5 Ohm resistor on 8/17/18

const float CLOCK_SPEED = 16.776 * pow(10, 6); // AD5933 has internal clock of 16.776 MHz

const int CONTROL_REGISTER[2] =                    { 0x80, 0x81       }; // see mapping below
const int START_FREQUENCY_REGISTER[3] =            { 0x82, 0x83, 0x84 }; // 24 bits for start frequency
const int FREQ_INCREMENT_REGISTER[3] =             { 0x85, 0x86, 0x87 }; // 24 bits for frequency increment
const int NUM_INCREMENTS_REGISTER[2] =             { 0x88, 0x89       }; //  9 bits for # of increments
const int NUM_SETTLING_CYCLES_REGISTER[2] =        { 0x8A, 0x8B       }; //  9 bits + 1 modifier for # of settling times
const int STATUS_REGISTER[1] =                     { 0x8F             }; // see mapping below
const int TEMPERATURE_DATA_REGISTER[2] =           { 0x92, 0x93       }; // 16-bit, twos complement format
const int REAL_DATA_REGISTER[2] =                  { 0x94, 0x95       }; // 16-bit, twos complement format
const int IMAG_DATA_REGISTER[2] =                  { 0x96, 0x97       }; // 16-bit, twos complement format

// control register map (D15 to D12)
const int DEFAULT_VALUE =                 B0000; // initial setting
const int INITIALIZE =                    B0001; // excite the unknown impedance initially
const int START_SWEEP =                   B0010; // begin the frequency sweep
const int INCREMENT =                     B0011; // step to the next frequency point
const int REPEAT =                        B0100; // repeat the current frequency point measurement
const int MEASURE_TEMP =                  B1001; // initiates a temperature reading
const int POWER_DOWN =                    B1010; // VOUT and VIN are connected internally to ground
const int STANDBY =                       B1011; // VOUT and VIN are connected internally to ground

const int BLOCK_WRITE = B1010000;
const int BLOCK_READ =  B1010001;
const int ADDRESS_PTR = 0xB0;// B1011000;

const int validTemperatureMeasurement =  1;
const int validImpedanceData =           2;
const int frequencySweepComplete =       4;

int temperatureData;

//functions declarations
int checkStatus();
boolean measureTemperature();
byte frequencyCode(float, int);
boolean setStartFrequency(float);
boolean setFrequencyIncrement(float);
boolean setNumberOfIncrements(int);
boolean setNumberOfSettlingTimes(int);
void measureImpedance();
void configureAD5933(int, float, float, int);
int getByte(int);
boolean setByte(int, int);
boolean setControlRegister(int);

boolean setControlRegister2();

int reading = 0;
byte rxByte;
int number;
char FirstChar[1];
char SecondChar[1];

int e = 0;
int y;
int ch;
int u;
int real;
int imag ;

long timeStamp;
long time1;
/////////////////////////////////////////////////////////////////////////////////
//    setup()
///////////////////////////////////////////////////////////////////////////////
void setup() {
  Wire.begin();
  Serial.begin(9600);
  wdt_enable(WDTO_2S);      // 2 second watch dog timer reset interval
  q.setup();

  pinMode(8, OUTPUT);   // mux
  pinMode(9, OUTPUT);   // on/off for conduino

  digitalWrite (8, LOW);     // set mux HIGH or LOW, it is not used
  digitalWrite (9, LOW);     // turn off conduino

  if (!SD.begin(4)) {
    q.setRGB(RED);    // SD card bad, turn on the red light
    wdt_reset();      // pet the dog
    delay(1000);
    return;
  }
  else {          // SD card is good, turn on the green light for 1 second
    q.setRGB(GREEN);
    wdt_reset();      // pet the dog
    delay(1000);
    q.ledOff();
  }

  wdt_reset();      // pet the dog

  sensors.begin();    // Initialize the temperature sensors
  sensor.initializeMS_5803();   // Initialize pressure sensor

  time1 = millis();     // initialize time stamp
}
/////////////////////////////////////////////////////////////////////////////////
//    loop() ~ 860ms
///////////////////////////////////////////////////////////////////////////////
void loop() {

  timeStamp += millis() - time1;
  time1 = millis();

  sensor.readSensor();    // read pressure sensor, takes 22ms

  // Read temperature sensors.
  sensors.requestTemperatures();      // takes 622 ms
  tempA = sensors.getTempCByIndex(0);
  tempB = sensors.getTempCByIndex(1);
  tempC = sensors.getTempCByIndex(2); // takes 126ms

  digitalWrite (9, HIGH);   // Conduino on
  delay (1);                // more than enough time to settle
  measureImpedance();       // get measurement from Conduino
  digitalWrite(9, LOW);     // Conduino off

  File dataFile = SD.open("datalog.txt", FILE_WRITE);   // takes ~4ms
  if (dataFile) {
    dataFile.print(timeStamp / 1000); dataFile.print(" ");
    dataFile.print(sensor.pressure()); dataFile.print(" ");
    dataFile.print(tempA); dataFile.print(" ");
    dataFile.print(tempB); dataFile.print(" ");
    dataFile.print(tempC); dataFile.print(" ");
    dataFile.print(Conductivity); dataFile.print(" ");
    dataFile.print(ConduinoReading, 4); dataFile.print(" ");  // raw number from conduino for calibration
    //dataFile.print(temperatureData); dataFile.print(" ");     // temperature from 5933 chip
    dataFile.println("");
    dataFile.close();
  }

  //    Write to serial monitor or not Comment/Uncomment
//      Serial.print(timeStamp / 1000); Serial.print(" ");
//      Serial.print (sensor.pressure()); Serial.print(" ");
//      Serial.print (tempA); Serial.print(" ");
//      Serial.print (tempB); Serial.print (" ");
//      Serial.print (tempC); Serial.print (" ");
//      Serial.print (Conductivity); Serial.print (" ");
//      Serial.print (ConduinoReading, 4); Serial.print(" ");  // for calibration
//      Serial.print(impedance); Serial.print (" ");
//      Serial.print (magnitude);
//      Serial.println("");

  while (millis() - time1 <= SampleInterval) { // wait for Sample Interval
    wdt_reset();              // reset the watchdog timer in case SampleInterval > 2000
  }
}
////////////////////////////////////////////////////////////////////////
//  Conduino Related Subroutines
////////////////////////////////////////////////////////////////////////
// message sequence:
// to set the memory address:
// 1. slave address
// 2. pointer command
// 3. register address to point to

// to write data (address already set):
// 1. slave address
// 2. block write
// 3. number bytes write
// 4. byte 0, byte 1, byte 2, etc.

// to read data (address is already set):
// 1. slave address with read bit high
// 2. register data is returned

// to read a block of data (address is already set):
// 1. slave address
// 2. block read
// 3. number of bytes
// 4. slave address (read bit high)
// 5. byte 0, byte 1, byte 2, etc.

// control register map (D10 to D9)
// ranges = {2.0 V p-p, 200 mV p-p, 400 mV p-p, 1.0 V p-p}

// control register map (D11, D8 to D0)
// D11 = no operation
// D8 = PGA gain (0 = x5, 1 = x1) // amplifies the response signal into the ADC
// D7 = reserved, set to 0
// D6 = reserved, set to 0
// D5 = reserved, set to 0
// D4 = reset // interrupts a frequency sweep
// D3 = external system clock, set to 1; internal system clock, set to 0
// D2 = reserved, set to 0
// D1 = reserved, set to 0
// D0 = reserved, set to 0

// number of increments register
// 0x88: D15 to D9 -- don't care
// 0x89: D8 -- number of increments bit 1
// 0x89: D7 to D0 -- number of increments bits 2 through 9; 9-bit integer number stored in binary format

// number of settling times
// 0x8A: D15 to D11 -- don't care
// 0x8A: D10 to D9 -- 2-bit decode
//        0 0 = default
//        0 1 = # of cycles x 2
//        1 0 = reserved
//        1 1 = # of cycles x 4
// 0x8A: D8 -- MSB number of settling times
// 0x8B: D7 to D0 -- number of settling times; 9-bit integer number stored in binary format

const int OUTPUT_VOLTAGE[4] = {
  B00, B01, B10, B11
};
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

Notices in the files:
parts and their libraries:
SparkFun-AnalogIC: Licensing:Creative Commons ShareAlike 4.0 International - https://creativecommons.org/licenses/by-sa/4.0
